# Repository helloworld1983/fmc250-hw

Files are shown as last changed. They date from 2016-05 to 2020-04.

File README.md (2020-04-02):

 FMC ADC 250M 16B 4CHA

## Project description

This project concerns the development of an ADC card in FMC (VITA 57)
format. The first intended application is the sampling RF signals in BPM
applications, as specified in the [BPM
project](https://www.ohwr.org/project/bpm/wiki).

-----

 Top view
*FMC ADC 250M 16B 4CHA production board**

-----

## Functional Specifications

  - VITA 57.1-2010 compliance
  - Four Channel 16 bit 250 MSPS ADC. Required ADC: ISLA216P25
  - Internal ADC clock circuit: phase locked to reference clock input
    with fine  
    frequency tuning capability. See specific section. Hold mode in case
    of loss of  
    external reference is a desirable feature.
  - Internal high frequency PLL oscillator output with amplitude control
    and locked  
    to external reference.
  - Reference clock can be sourced from front panel or from FMC pins
    CLK2\_BIDIR  
    and CLK3\_BIDIR
  - The FMC pin CLK\_DIR shall be connected to 3P3V via a 10KΩ pull up
    resistor to  
    indicate CLK2\_BIDIR and CLK3\_BIDIR are driven from the carrier to
    the FMC  
    mezzanine.
  - External ADC clock input (50 MHz up to 250 MHz, 0 dBm typ.)1
  - External reference clock input: (0.5 MHz - 20 MHz digital signal, 0
    dBm typ.)2
  - External digital trigger input

-----

## Detailed Project Information

  - Documentation:
      - Schematics
        ([PDF](https://www.ohwr.org/project/fmc-adc-250m-16b-4cha/blob/master/fmc-adc-250m-16b-4cha/SCH_FMC_ADC_250M_16B_4ch.pdf),
        [Altium
        sources](https://www.ohwr.org/project/fmc-adc-250m-16b-4cha/tree/master/fmc-adc-250m-16b-4cha/Schematics))
      - PCB
        ([PDF](https://www.ohwr.org/project/fmc-adc-250m-16b-4cha/blob/master/fmc-adc-250m-16b-4cha/PCB_FMC_ADC_250M_16B_4ch.pdf),
        [Altium
        sources](https://www.ohwr.org/project/fmc-adc-250m-16b-4cha/blob/master/fmc-adc-250m-16b-4cha/FMC_ADC_250M_16B_4ch_pcb.PcbDoc))

<!-- end list -->

  - [Block
    diagram](https://www.ohwr.org/project/fmc-adc-250m-16b-4cha/uploads/cf81ca76566ecf84ca79289acfed6a32/FMC_ADC.png)
  - [Users](Users)

-----

## Contacts

### commercial producers

  - [Creotech](http://creotech.pl/product-scientific/fmc-adc-250m-16b-4cha),
    Poland

### General question about project

  - [Filip Świtakowski](mailto:filip.switakowski@creotech.pl)

-----

## Status

|**Date**|**Event**|
|----|----|
|01-09-2012|Start working on project|
|01-10-2012|First version of schematics and PCB component placement|
|17-11-2012|Schematic review|
|19-11-2012|Schematic bugs fixed, final component placement, added heatsink anad start of PCB routing|
|23-11-2012|Board 100% routed. Heat sink design sent to the mechanical workshop for verification.|
|18-02-2013|Boards delivered, still waiting for heat sinks and panels|
|20-05-2013|Boards fully tested and working. Small issues with S11 caused by baluns and 2V5 supply that is not sufficient for LDOs. With 3V3 works fine|
|30-09-2014|v1.1 tested & working|

-----

Filip Świtakowski 04 Feb 2014

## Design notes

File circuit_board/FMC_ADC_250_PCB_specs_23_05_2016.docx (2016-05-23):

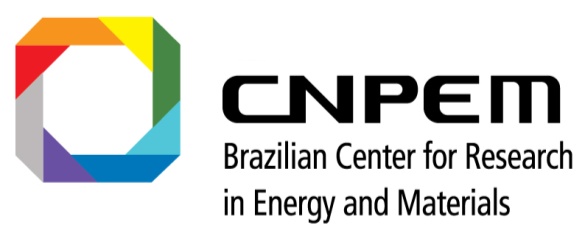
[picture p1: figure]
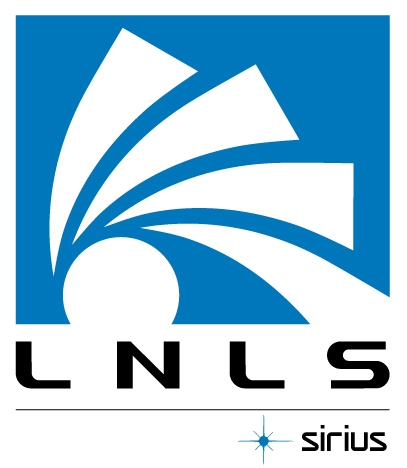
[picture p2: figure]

Manufacturing specifications for the FMC_ADC_250M hardware

May 2016

Beam Diagnostics Group (DIG)

BLANK PAGE

# PCB Fabrication Specification

Design references
Name | FMC_ADC_250M | Date: | 05/23/2015
File name
Designers | Fernando Cambauva SantAnna
E-mail | fernando.santanna@lnls.br
Fone | +55 19 3512-5071
Cel | +55 16 99206-8595

Mechanical characteristics
External size (mm) | 77 x 69 mm
Thickness (mm) | 1.4 mm
Layers | 8
Min track width (mm/mils) | 0.05mm / 2mils
Min Hole size (mm/mils) | 0.2mm / 7.8mils
Laminate | FR-4 – TG150
Pre-preg | FR-4 – TG150

Finish Copper
External layers (µm) | 35 µm
Holes walls (µm) | 25 µm
Internal Layers-Planes (µm) | 35 µm
Internal Layers-Signals (µm) | 35 µm

Board finishing requirements
Mask Solder color | Red for prototype and Blue for production
Silkscreen on top layer (color) | White
Silkscreen on bottom layer (color) | White
Surface Finishing | ENIG – Electroless Nickel / Immersion Gold according to IPC-4552
Thickness | Ni: 3 µm min, 6 µm máx. Au: 0.05 µm min, 0.125 µm máx

Additional Information
Impedance test | No
Packaging requirements | No
Documentation to be delivered | No
Additional control quality requirements | No

| Board Stackup Information
| Name: | | Laminate/pre-preg | Thickness (mm/mils)
Layer 1 | Top Layer | RF signals
Layer 2 | GND(SMAGND) | RF Ground Plane | FR-4 | 0.11mm
Layer 3 | L3 | Digital signals | FR-4 | 0.1mm
Layer 4 | GND2 | RF Ground Plane + Digital Ground plane | FR-4 | 0.29mm
Layer 5 | L5 | Digital signals | FR-4 | 0.1mm
Layer 6 | GND3 | RF Ground Plane + Digital Ground plane | FR-4 | 0.29mm
Layer 7 | Power | Power | FR-4 | 0.1mm
Layer 8 | Bottom Layer | Digital signals | FR-4 | 0.11mm
Total | | | Total | 1.515 mm

Centro Nacional de Pesquisa em Energia e Materiais (CNPEM) Laboratório Nacional de Luz Síncrotron (LNLS) Rua Giuseppe Maximo Scolfaro, 10000, Polo II de Alta Tecnologia Campinas, São Paulo, Brazil CEP 13083-970 – Caixa Postal 6192

Last update: 23 May 2016 - 15:59 4

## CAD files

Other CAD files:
MECH/Heatsink FMC 250v2_4.ipt
MECH/Panel FMC v4.1.ipt
MECH/SMA Isolator v3.ipt

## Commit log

2012-10-01 initial version of schematics, first placement of critical components
    [ADC.SchDoc, Clock_Distribution.SchDoc, EEPROM_Temp_LEDs.SchDoc, FMC_ADC_250M_16B_4ch.PrjPCB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]
2012-11-14 improved symmetry between channels
    [ADC.SchDoc, ADC_Buffers.SchDoc, Clock_Distribution.SchDoc, EEPROM_Temp_LEDs.SchDoc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]
2012-11-19 improved symmetry of the channels. Added die-casted shield + heatsink fixed schematic bugs after review added voltage level translator/buffer between FPGA and ADC improved signal integrity of clock c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
    [ADC.SchDoc, ADC_Buffers.SchDoc, Clock_Distribution.SchDoc, EEPROM_Temp_LEDs.SchDoc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]
2012-11-20 almost done, some control tracks missing and cosmetic cleaning needed
    [ADC.SchDoc, ADC_Buffers.SchDoc, Clock_Distribution.SchDoc, Supply.SchDoc]
2012-11-21 routed. Cosmeting cleaning required. Still need to check some rules.
    [Clock_Distribution.SchDoc, EEPROM_Temp_LEDs.SchDoc, FMC_ADC_250M_16B_4ch.PrjPCB, FMC_connector.SchDoc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]
2012-11-22 final version, needed to be prepared for production heatsink design needed as well
    [FMC_connector.SchDoc]
2012-11-23 added heatsink/shield
    [FMC_ADC_250M_16B_4ch.PrjPCB, shield.PcbDoc]
2012-11-25 added OHWR license note on each schematic
    [ADC.SchDoc, ADC_Buffers.SchDoc, Clock_Distribution.SchDoc, EEPROM_Temp_LEDs.SchDoc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]
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2012-12-14 fixed bugs in clock distribution, unified shield - same as in 130MHz FMC ADC
    [Clock_Distribution.SchDoc, FMC_ADC_250M_16B_4ch.PrjPCB]
2013-01-07 fixed most of the issues - added 0R resistors for clock option selection, added silkscreen, logos.
    [ADC.SchDoc, Clock_Distribution.SchDoc, FMC_ADC_250M_16B_4ch.PrjPCB, FMC_ADC_top.SchDoc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]
2013-01-24 added machined FMC panel, added GND layer for better copper balancing on L3, added cutouts under SMA pins and input tracks, fixed silkscreen, fixed SMA connector layout - paste and soldermask opening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
    [ADC.SchDoc, ADC_Buffers.SchDoc, FMC_ADC_250M_16B_4ch.PrjPCB, FMC_ADC_top.SchDoc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]
2014-06-28 rev 1.1 clock mux bias ADC LDO supply - 3.3 vs VADJ balun bypass
    [ADC.SchDoc, Clock_Distribution.SchDoc, EEPROM_Temp_LEDs.SchDoc, FMC_ADC_250M_16B_4ch.PrjPCB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]
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2016-03-11 Change name of project to LNLS
    new desing changes began in this repository
    [FMC_ADC_250M_16B_4ch_LNLS.PrjPCB]
2016-03-11 change SMA GND connection to avoid ground loop.
    only in SCH
    [ADC.SchDoc, FMC_ADC_top.SchDoc]
2016-03-11 Change footprint pins for PMGD280UN Q1;2;3
    same error in fmc 130
    [EEPROM_Temp_LEDs.SchDoc, Triggers.SchDoc]
2016-03-11 gitignore file
    [FMC_ADC_250M_16B_4ch_LNLS.PrjPCB]
2016-04-14 modify SCH to new components and variants
    -change pairs FMC_CLK > CLK3_BIDIR to CLK2_BIDIR
    -change IC4 to ICS854S01AKILF same using on FMC130 REF clock IN
    -Add new variants name to LNLS
    [ADC.SchDoc, Clock_Distribution.SchDoc, FMC_ADC_250M_16B_4ch_LNLS.PrjPCB, FMC_connector.SchDoc]
2016-04-14 change loop filter values
    New values to loop filter circuit components. That are same of FMC 130
    [Clock_Distribution.SchDoc, FMC_ADC_250M_16B_4ch_LNLS.PrjPCB]
2016-04-18 initial changes on PCB
    [ADC.SchDoc, Clock_Distribution.SchDoc, FMC_ADC_top.SchDoc, FMC_connector.SchDoc]
2016-04-19 changed the channel "A" and the position of tracks
    router tracks of the new CI IC4
    [FMC_ADC_250M_16B_4ch_LNLS.PrjPCB, FMC_connector.SchDoc]
2016-04-20 New frontend circuit optimized for ~500Mhz
    [ADC.SchDoc]
2016-04-20 make channel "A" on PCB
    [ADC.SchDoc]
2016-04-25 removed transformer bypass caps
    [ADC.SchDoc]
2016-04-25 TR1 add 0R in 9 and 10 pins
    [ADC.SchDoc]
2016-05-02 Add IC5 PCA9306DCTR in i2c bus for isolation
    [Clock_Distribution.SchDoc]
2016-05-02 Add IC5 PCA9306DCTR in i2c bus for isolation on PCB
    [Clock_Distribution.SchDoc]
2016-05-11 Added protection circuit for high peeks 3v3 x VADJ
    Added protection circuit for high peeks 3v3 x VADJ
    [Clock_Distribution.SchDoc, FMC_connector.SchDoc]
2016-05-11 Added protection circuit for high peeks - PCB
    [Clock_Distribution.SchDoc, FMC_connector.SchDoc]
2016-05-16 DRC check
    [ADC.SchDoc, FMC_ADC_250M_16B_4ch_LNLS.PrjPCB, FMC_ADC_top.SchDoc, FMC_connector.SchDoc]
2016-05-16 Modify tracks to width 0.508mm on SMA input
    [FMC_ADC_250M_16B_4ch_LNLS.PrjPCB]
2016-05-20 Changed Supply.SchDoc capacitors to new library
    10uF and 1uF capacitors on Supply.SchDoc were changed to the new library.
    [Supply.SchDoc]
2016-05-23 update production document and mechanical parts
    [Painel FMC 250 v2.stp, Painel FMC v4 anel de silicone Amarelo.ipt, Painel FMC v4 anel de silicone Amarelo.stp, Painel FMC v4 anel de silicone Azul.ipt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]
2016-05-24 new 2d Shield and frontend SMA GND
    [FMC_ADC_250M_16B_4ch_LNLS.PrjPCB]
2016-05-24 Changed resistors in Clock_distribution.SchDoc to new library
    [Clock_Distribution.SchDoc]
2016-05-25 missing pcbdoc modifications
    [FMC_ADC_250M_16B_4ch_LNLS.PrjPCB]
2016-05-25 Removed R5 0-Ohm resistor bw Anaren and GND
    This aims to improve electrical contact between the balun and GND, also
    helping shield design.
    [ADC.SchDoc]
2016-05-25 Changed GND_ADC net name to GND_SMA
    [ADC.SchDoc, FMC_ADC_top.SchDoc]
2016-05-28 Update 200R 5% 0402 resistors to new lib
    [Clock_Distribution.SchDoc]
2016-05-28 Finished updating all resistors on the board
    [Clock_Distribution.SchDoc, Supply.SchDoc]
2016-05-28 Changed IC19 symbol to new library
    [Supply.SchDoc]
2016-05-28 Changed IC18 to new lib
    [FMC_ADC_top.SchDoc]
2016-05-28 Changed IC14 to new library
    [Supply.SchDoc]
2016-05-28 Miscellaneous library updates
    [ADC.SchDoc, Clock_Distribution.SchDoc, Triggers.SchDoc]
2016-05-29 Changed IC20 for new library
    [Triggers.SchDoc]
2016-05-29 Updated IC4 to new lib
    [Clock_Distribution.SchDoc]
2016-05-31 Changed NMOD PMG transistors to new lib
    [EEPROM_Temp_LEDs.SchDoc, Triggers.SchDoc]
2016-05-31 Update all parameters of new components
    [ADC.SchDoc, ADC_Buffers.SchDoc, Clock_Distribution.SchDoc, EEPROM_Temp_LEDs.SchDoc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]
2016-05-31 Updated SMA connectors to new lib
    [FMC_ADC_top.SchDoc]
2016-06-01 Changed inductor and capacitor in ADC AFE
    [ADC.SchDoc, ADC_Buffers.SchDoc, Clock_Distribution.SchDoc, EEPROM_Temp_LEDs.SchDoc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]
2016-06-01 Updated ADC buffers to new library
    [ADC.SchDoc, ADC_Buffers.SchDoc, Clock_Distribution.SchDoc, EEPROM_Temp_LEDs.SchDoc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]
2016-06-01 Corrected keepout layer.
    [FMC_ADC_top.SchDoc, FMC_connector.SchDoc]
2016-06-07 add new components by library
    [ADC_Buffers.SchDoc, Clock_Distribution.SchDoc, FMC_ADC_250M_16B_4ch_LNLS.PrjPCB, FMC_ADC_top.SchDoc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]
2016-06-07 Setup BOM to LNLS DIG standard
    [FMC_ADC_250M_16B_4ch_LNLS.PrjPCB]
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2016-06-15 Changed R132 size to reduce different part numbers
    [FMC_connector.SchDoc]
2016-06-15 Changed R44 and R55 to same PN as R1
    [Clock_Distribution.SchDoc]
2016-06-15 Changed R45, R74 and R75 to same PN as R3
    [Clock_Distribution.SchDoc, FMC_connector.SchDoc]
2016-06-15 Changed all 10nF capacitors to same size X7R
    [ADC_Buffers.SchDoc, Clock_Distribution.SchDoc, Triggers.SchDoc]
2016-06-15 Corrected Part Number for D3, D4, D5 and D6
    [FMC_connector.SchDoc]
2016-06-15 Corrected OSC2 library component
    [Clock_Distribution.SchDoc]
2016-06-15 some corrections on PCB
    new footprints
    [FMC_ADC_top.SchDoc]
2016-06-16 Updated clock distribution
    Removed passive clocks and supporting components, added rules for clock
    lengths.
    [Clock_Distribution.SchDoc]
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2016-06-16 Corrected Ic18 to fit library
    [FMC_ADC_top.SchDoc]
2016-06-20 Corrected R26, R31 and R36 mounted parameter
    Changed Mounted to Yes and set R26 as not fitted in LNLS-active variant.
    [Clock_Distribution.SchDoc, FMC_ADC_250M_16B_4ch_LNLS.PrjPCB]
2016-06-20 Changed project folder structure.
    [ADC.SchDoc, ADC_Buffers.SchDoc, Clock_Distribution.SchDoc, EEPROM_Temp_LEDs.SchDoc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]
2016-06-20 Removed peripheral from OSC1 from LNLS variant
    [Clock_Distribution.SchDoc, FMC_ADC_250M_16B_4ch.PrjPCB]
2016-06-20 Reverted uncorrect change of IC18 part.
    [FMC_ADC_top.SchDoc]
2016-06-20 Changed C131 footprint to match similar capacitors
    [FMC_ADC_250M_16B_4ch.PrjPCB, Triggers.SchDoc]
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2016-06-22 config BOM export
    [FMC_ADC_250M_16B_4ch.PrjPCB]
2016-06-22 add Power columns on BOM export
    [FMC_ADC_250M_16B_4ch.PrjPCB]
2016-07-13 change C38 and C59 to 25v for compatible with RFFE components
    [ADC.SchDoc, Clock_Distribution.SchDoc]
2017-01-12 Improvements in the AFE
    [ADC.SchDoc]
2017-01-12 Changed ref clock input to allow a variet of inputs
    [Clock_Distribution.SchDoc]
2017-01-13 Add Resistor on REF Clk IN and removed on Anaren
    [FMC_ADC_250M_16B_4ch.PrjPCB]
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2017-01-27 Corrected variants
    [Clock_Distribution.SchDoc, FMC_ADC_250M_16B_4ch.PrjPCB]
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2017-03-02 Correct SMA connectors part number
    Removed 6RFX suffix, which refers to a different part than intended.
    [FMC_ADC_top.SchDoc]
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2017-05-09 Corrected L8 value to 1.8uH
    [Supply.SchDoc]
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
